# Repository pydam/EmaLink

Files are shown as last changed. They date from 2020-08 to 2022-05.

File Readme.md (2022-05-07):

# EmaLink

A device that bridges the communication between Loop software application and Omnipod and Medtronic insulin pumps. This is a fork from RileyLink, focusing on reducing size of the device, improving communication range and extending battery life. Also, you can charge EmaLink with any micro USB charger - much broader available vs. the mini port USB used by RileyLink.

### Turning on
Use a nail, a small plastic or a wood bit to move the power switch towards the USB port. When EmaLink is powered on, you should see a red and a green LED turning on for 1 second.

### Connecting EmaLink to Loop/FreeAPS/AndroidAPS
Please follow the instructions provided by each application for connecting to EmaLink, the procedure is the same as for RileyLink, just the name of the device will be EmaLink.Once EmaLink is connected to Loop/FreeAPS/AndroidAPS, a green led will start blinking every 3 seconds on EmaLink.

### Charging

Once the battery gets almost depleted, a red led will start blinking every 3 seconds.
To charge it, you can use any micro USB charger from a phone, tablet, headset or another device. You can even use a power bank to charge it if it has a micro USB cable. Charging is considered finished after the red led (the one close to the USB connector) is turned off. It may take up to 3 hours for Nano.
For QI versions, charging can be also done with any QI compatible charge. Place EmaLink with the coil (you can see a round, copper coil, through the case) down on the middle of the QI charger and check that a red led is lighting from the top of the EmaLink. Once charging is completed, you should remove EmaLink from the charger as the charger reduces communication range.
Charging can be done every few days until EmaLink is fully charged (the red led turned off) or for a few minutes every day, depending on your schedule. Overnight charging also works well with a Micro USB charge but avoid leaving QI versions on the QI charger overnight as this reduced communication range and may generate red loops.

### LED Lights 

There are 3 leds on the back of the device: a red one, close to the micro USB charging port, and a red + green cluster on the other side. First, turn the EmaLink on by flipping the switch located next to the micro USB port. After you switch-on EmaLink, the red + green cluster will light-up for 1 second. When you connect EmaLink to AAPS on Loop over bluetooth, the green led will start blinking every 3 seconds. The green led will stop blinking once battery is almost depleted. The red led will start blinking once battery is almost depleted, you should consider charging it in the next few hours.

### Case

I have designed a new case to be 3D printed with TPU material. TPU is a flexbile material that cannot be shattered, this makes EmaLink
drop proof. There are several case styles to chose from, pick the one that makes most sense for your needs.

### Hardware

See the [hardware](https://github.com/sks01/emalink/tree/master/hardware) directory for design files to build it. The hardware design is released under [Creative Commons Share-alike 3.0](http://creativecommons.org/licenses/by-sa/3.0/).  

### Firmware

The code in the [firmware](https://github.com/sks01/emalink/tree/master/firmware) directory runs on the hardware.  There are two main chips and thus two firmware images.
Check the "EmaLink 3_7 3_8 - firmware update guide.docx" if you would like to understand how you can update the firmware for EmaLink with PCB version 3.7, 3.8 or 3.9.

Check the "EmaLink 3_2 3_3 - firmware update guide.docx" if you would like to understand how you can update the firmware for EmaLink with PCB version 3.2 or 3.3. You can use breadboard wires also but you may need to keep them at an angle while flashing as the PCB holes are slightly bigger.

Check the "EmaLink%204_4%20-%20firmware%20update%20guide.pdf" if you would like to understand how you can update the firmware for EmaLink with PCB version 4.x. 

### License

The MIT License (MIT)

Copyright (c) 2015 Pete Schwamb

Permission is hereby granted, free of charge, to any person obtaining a copy
of this software and associated documentation files (the "Software"), to deal
in the Software without restriction, including without limitation the rights
to use, copy, modify, merge, publish, distribute, sublicense, and/or sell
copies of the Software, and to permit persons to whom the Software is
furnished to do so, subject to the following conditions:

The above copyright notice and this permission notice shall be included in all
copies or substantial portions of the Software.

THE SOFTWARE IS PROVIDED "AS IS", WITHOUT WARRANTY OF ANY KIND, EXPRESS OR
IMPLIED, INCLUDING BUT NOT LIMITED TO THE WARRANTIES OF MERCHANTABILITY,
FITNESS FOR A PARTICULAR PURPOSE AND NONINFRINGEMENT. IN NO EVENT SHALL THE
AUTHORS OR COPYRIGHT HOLDERS BE LIABLE FOR ANY CLAIM, DAMAGES OR OTHER
LIABILITY, WHETHER IN AN ACTION OF CONTRACT, TORT OR OTHERWISE, ARISING FROM,
OUT OF OR IN CONNECTION WITH THE SOFTWARE OR THE USE OR OTHER DEALINGS IN THE
SOFTWARE.

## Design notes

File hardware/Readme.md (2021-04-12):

# EmaLink Hardware

 *  Project_EL v4.3_2021-04-12_19-27-16.zip - EasyEDA project for version 4.3
 *  Schematic_EL v4.x.pdf - Schematic for versions 4.1-4.2
 *  Project_EL v4.1.zip - EasyEDA project for versions 4.1-4.2
 *  Gerber_EL v4.2 PCB.zip - Gerber files for version 4.2
 
### PCB Assembly

You will have to look at the schematic and the board design in Kicad to know where the parts go, and how they are oriented.

I use a hot-air rework station to solder the BLE113 module, the CC1110 chip, the USB connector, the 24Mhz crystal and the 3 power coils. The rest can be soldered with normal soldering station but require good soldering skills (especially the balun and the RF tuning network)

### License

The hardware design is released under [Creative Commons Share-alike 3.0](http://creativecommons.org/licenses/by-sa/3.0/).

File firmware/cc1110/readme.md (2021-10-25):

*  CC1110 firmware version 2.2.23 works only with BLE firmware 3.15 or above. Also, PCB version v4.0 or above is needed for these firmware versions.
*  CC1110 firmware version 2.2.22 works only with BLE firmware 3.15 or above. Also, PCB version v4.0 or above is needed for these firmware versions.
*  CC1110 firmware version 2.2.21 works only with BLE firmware 3.13. Also, PCB version v4.0 or above is needed for these firmware versions.
*  CC1110 firmware version 2.2.19 works only with BLE firmware 3.11

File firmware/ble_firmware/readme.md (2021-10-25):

*  BLE firmware version 3.17 and 3.18 version works only with CC1110 2.2.22 or 2.2.23 firmware. Also, PCB version v4.0 or above is needed for these firmware versions.
*  BLE firmware version 3.15 version works only with CC1110 2.2.22 firmware. Also, PCB version v4.0 or above is needed for these firmware versions.
*  BLE firmware version 3.13 version works only with CC1110 2.2.21 firmware. Also, PCB version v4.0 or above is needed for these firmware versions.
*  BLE firmware version 3.11 version works only with CC1110 2.2.19 firmware

The BLE firmware needs to be be unpacked and adjusted to offer best battery charge indication.

You will need to adjust 2 areas:
*  in file main.bgs, go through the sections that start with "#look-up table for..." and uncomment the one that seems to be for your battery. Contact the author if you don't manage to identify the right one based on the battery your EmaLink has. If you select another section versus the one selected by default, make sure to unselect the default section or you will get compilation errors.
*  in file main.bgs, search for "const voltage_adj =". You will need to replace the value 1000 with the value that is specific to your EmaLink. You can use the value noted in a corner of the EmaLink PCB, a value in between 970 and 1030. Or, execute the procedure below in case that value is not visible anymore.
*  measure current battery voltage with a multimeter. If the value is above 4.17v, you need to use EmaLink until the voltage drops a bit.
*  check the voltage as reported by EmaLink; to get the voltage from EmaLink, you need to connect to EmaLink with some BLE tool (I use BLE Scanner) and read the "BATTERY VOLTAGE" customer Characteristic, under the CUSTOM SERVICE offered by EmaLink. This is shown as a 16bit hex number. Convert it to decimal and divide by 100 to see the battery voltage (for ex., 0x0170 = 3.68v)
*  Once you have them both, calculate the factor as [measured battery voltage]/[reported battery voltage]1000. So if you have measured 4.16v while EmaLink reports 4.12v, you need a factor of 4.16/4.121000 = 1009. Edit main.bgs file to have "const voltage_adj = 1009" and flash again the firmware on BLE chip. 
*  Repeat the cycle, until the [measured battery voltage]=[reported battery voltage]

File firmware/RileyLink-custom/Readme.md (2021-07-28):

*  Use the RileyLink firmware update guides to update your RileyLink with the custom EmaLink firmware versions. 
*  The immediate change you will see, is that the green led will blink every 3 seconds when RileyLink is connected over Bluetooth. No other LED will turn on while using RileyLink.
*  There is no indication when you battery get almost depleted, plan to charge your RileyLink on a regular basis. You can see details about expected battery lifetime between changes in the Wiki pages.

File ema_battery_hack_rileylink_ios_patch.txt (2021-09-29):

diff --git a/RileyLinkBLEKit/RileyLinkDevice.swift b/RileyLinkBLEKit/RileyLinkDevice.swift
index 412404d..d01bb68 100644
--- a/RileyLinkBLEKit/RileyLinkDevice.swift
+++ b/RileyLinkBLEKit/RileyLinkDevice.swift
@@ -14,7 +14,10 @@ public enum RileyLinkHardwareType {
     case ema
     
     var monitorsBattery: Bool {
-        return self == .orange
+        if self == .riley {
+            return false
+        }
+        return true
     }
 }
 
@@ -91,6 +94,9 @@ public class RileyLinkDevice {
         
         if services.itemWithUUID(RileyLinkServiceUUID.secureDFU.cbUUID) != nil {
             return .orange
+        } else if services.itemWithUUID(RileyLinkServiceUUID.battery.cbUUID) != nil {
+            // this returns true for riley with ema firmware, need a different check
+            return .ema
         } else {
             return .riley
         }
diff --git a/RileyLinkKitUI/RileyLinkDeviceTableViewController.swift b/RileyLinkKitUI/RileyLinkDeviceTableViewController.swift
index 9fae599..c082249 100644
--- a/RileyLinkKitUI/RileyLinkDeviceTableViewController.swift
+++ b/RileyLinkKitUI/RileyLinkDeviceTableViewController.swift
@@ -137,7 +137,7 @@ public class RileyLinkDeviceTableViewController: UITableViewController {
         title = device.name
         
         switch device.hardwareType {
-        case .riley, .ema, .none:
+        case .riley, .none:
             deviceRows = [
                 .customName,
                 .version,
@@ -147,6 +147,21 @@ public class RileyLinkDeviceTableViewController: UITableViewController {
                 .frequency
             ]
             
+            sections = [
+                .device,
+                .rileyLinkCommands
+            ]
+        case .ema:
+            deviceRows = [
+                .customName,
+                .version,
+                .rssi,
+                .connection,
+                .uptime,
+                .frequency,
+                .battery
+            ]
+
             sections = [
                 .device,
                 .rileyLinkCommands
@@ -297,6 +312,9 @@ public class RileyLinkDeviceTableViewController: UITableViewController {
         switch device.hardwareType {
         case .riley:
             readDiagnosticLEDMode()
+        case .ema:
+            device.updateBatteryLevel()
+            readDiagnosticLEDMode()
         case .orange:
             device.updateBatteryLevel()
             device.orangeWritePwd()

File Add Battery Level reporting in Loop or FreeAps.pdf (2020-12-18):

## Background

EmaLink hardware and firmware was improved to report the estimate remaining battery capacity. The estimate is not perfect but should still be a decent indicator of remaining battery life. In order to see the remaining charge in Loop or FreeAps, you need to implement some changes to one of its components: rileylink_ios. There are 2 ways to do it, both require some software skills.

## Solution 1 (medium): use a different rileylink_ios in your build

Steps:
- start from Loop dev branch
- in the Cartfile, change from github "ps2/rileylink_ios" "dev" to github "Andrei0105/rileylink_ios" "battery-dev"
- delete cartfile.resolved or execute carthage update
- build loop; first build may fail but the second build always works

## Solution 2 (hard): create a patch for your rileylink_ios of choice

Apply this patch below to the rileylink_ios that you want to use. This may require some changes as rileylink_ios code might be already different

https://github.com/Andrei0105/rileylink_ios/commit/bdadeebf08977e7428b871b4ec696280328220d8

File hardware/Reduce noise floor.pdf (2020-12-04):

## Background

In some situations, the noise generated by the onboard switching power supply, is picked-up by the radio receiver and negatively impacts the communication between EmaLink and your pump. This was mostly observed with Omnipod versions of EmaLink.

All EmaLinks manufactured as of 22-Nov-2020 have be improved and tested to eliminate this potential issue.

## Solution 1 (hard): Filter battery ground

Tools and parts needed:
a. Soldering station
b. Soldering wire
c. A power inductor with inductance of 1.5-4.7uH and DC resistance of maximum 0.1ohm. See below some options that would work:
i. LBR2518T2R2M – available from DigiKey or Mouser
ii. DFE201612E-1R5M - available from DigiKey, Mouser or Farnell
Steps:

### 1. Put a solder blob on the left pad of the USB filtering capacitor

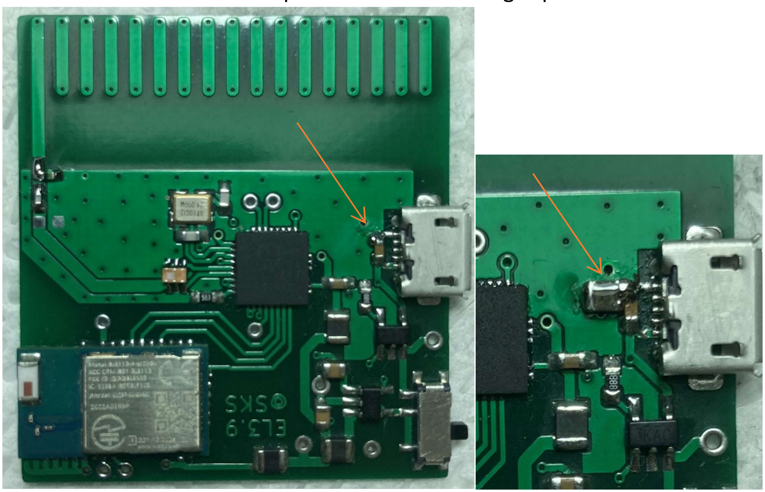
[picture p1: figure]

### 2. Solder one pad of the inductor to that solder blob

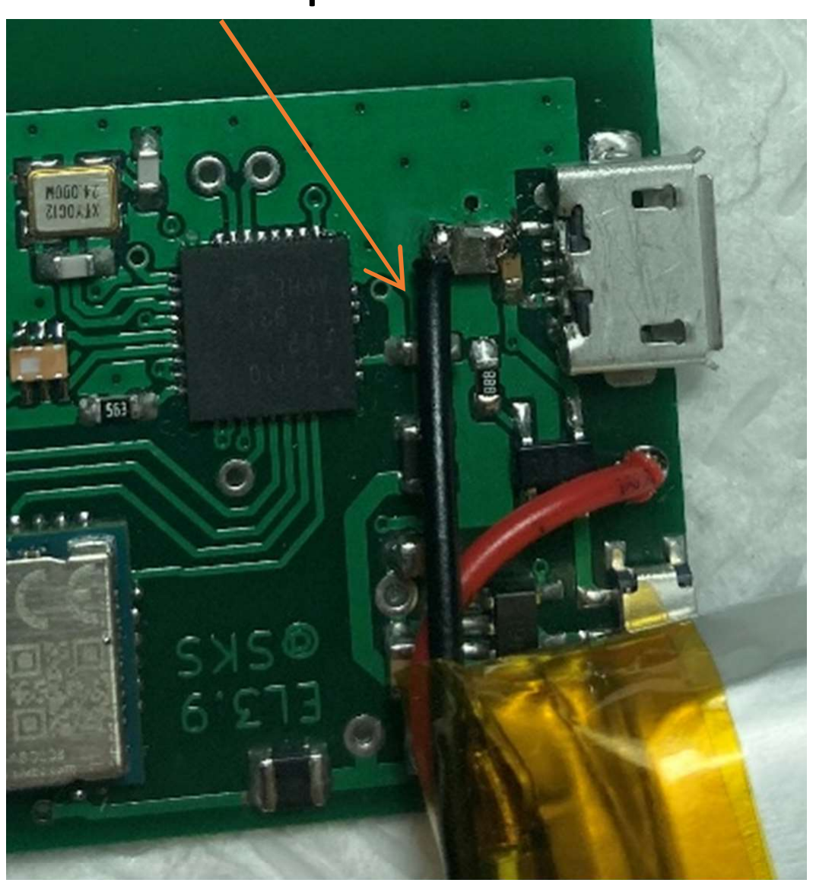
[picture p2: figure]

3. Unsolder the black battery wire from current position and solder it to the free pad of the inductor

## Solution 2 (easy): Increase gap between battery and CC1110

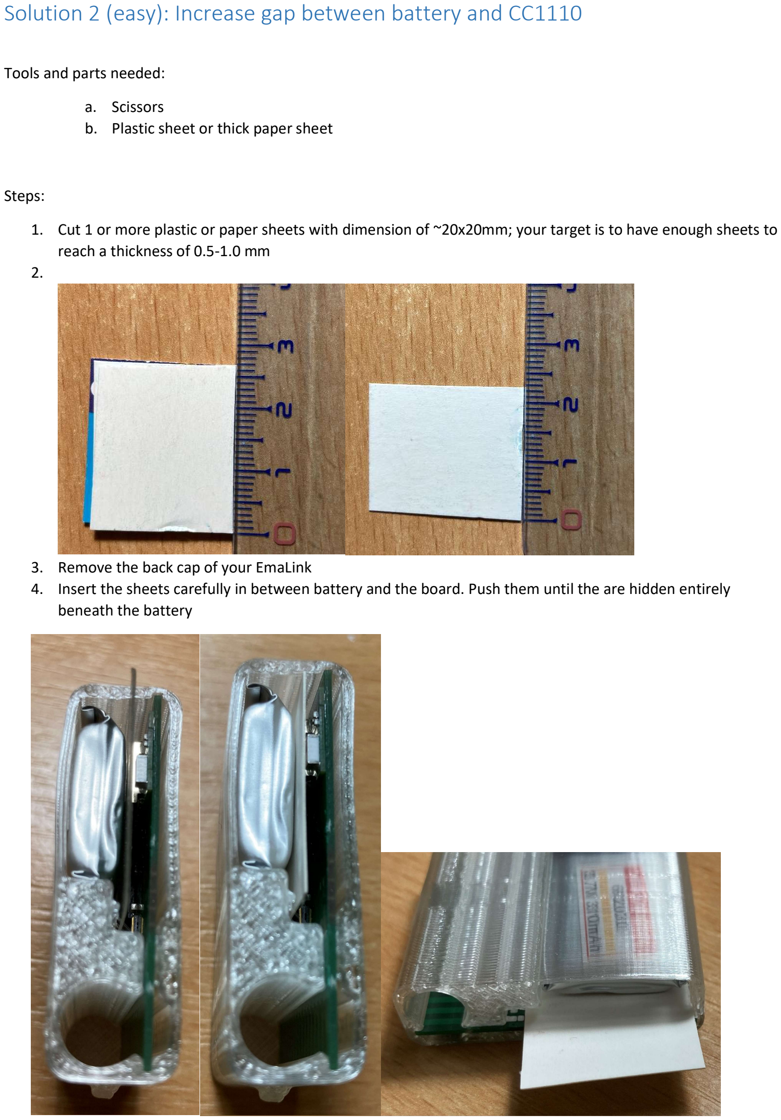
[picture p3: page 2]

Tools and parts needed:
a. Scissors
b. Plastic sheet or thick paper sheet

Steps:
1. Cut 1 or more plastic or paper sheets with dimension of ~20x20mm; your target is to have enough sheets to reach a thickness of 0.5-1.0 mm
2.

### 3. Remove the back cap of your EmaLink

4. Insert the sheets carefully in between battery and the board. Push them until the are hidden entirely beneath the battery

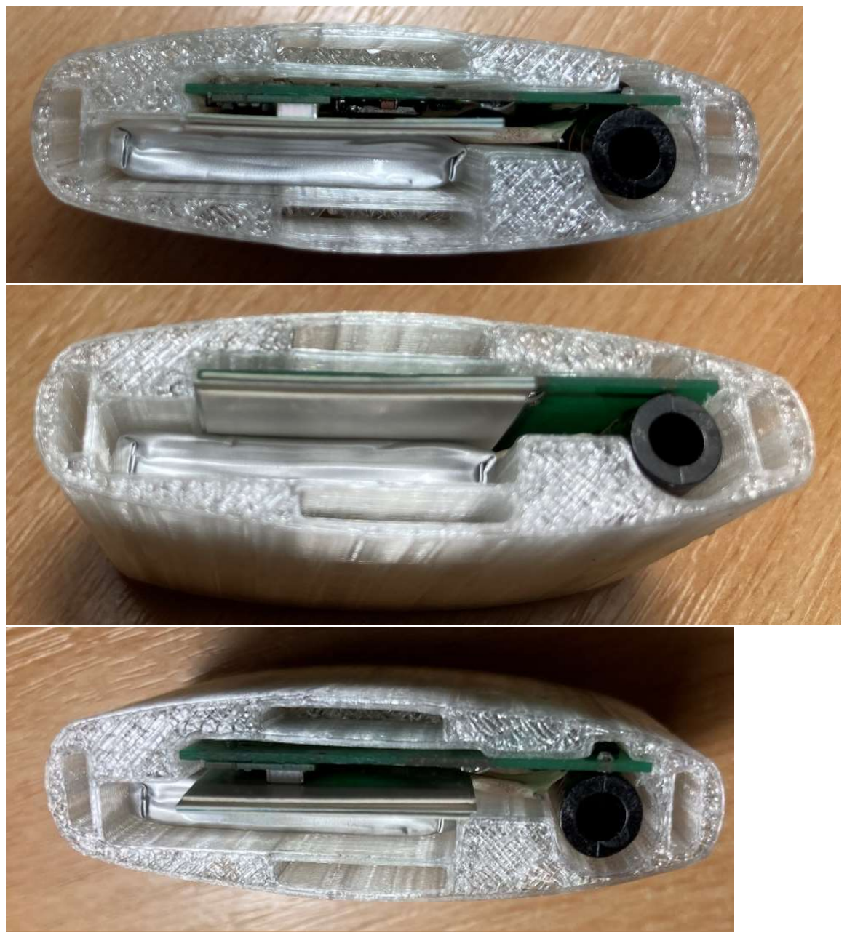
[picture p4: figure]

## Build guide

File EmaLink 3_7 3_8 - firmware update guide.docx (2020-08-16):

Prerequisites:

- CC Debugger (original (https://ro.farnell.com/texas-instruments/cc-debugger/debuggerprogrammer-for-rf-soc/dp/3009896?scope=partnumberlookahead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) – 50Euro or clone (https://www.ebay.com/itm/CC-Debugger-Bluetooth-ZigBee-Emulator-For-2530-2531-2540-2541-protocol-analysis/402021598624) 10-25Euro)
- Computer with Microsoft Windows 10 and at least one USB port available to connect
- SmartRF Studio from http://www.ti.com/tool/smartrftm-studio (Make sure to 'Extract All' if prompted at install/unzip time) ; you will need an account to download it
- http://www.ti.com/tool/FLASH-PROGRAMMER - install the old 1.12.8 version; you will need an account to download it

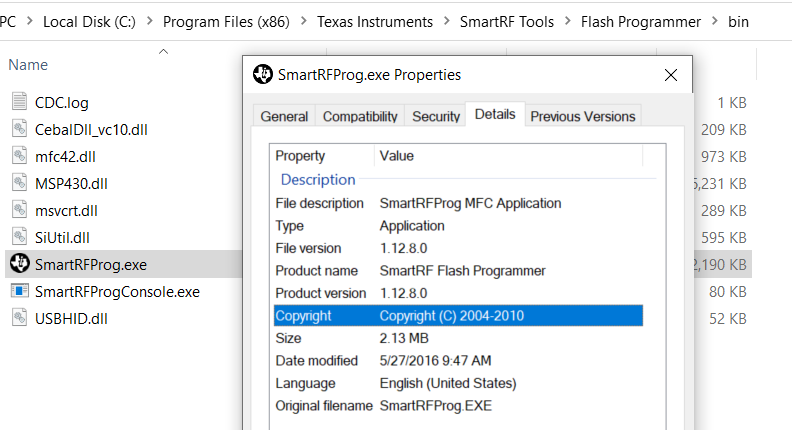
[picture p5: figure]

- "Bluetooth Smart Software and SDK v.1.8.0" (or above) from (https://www.silabs.com/documents/login/software/Bluegiga_ble-1.8.0-143.exe)
- 4 breadboard wires with a 0.6 tip

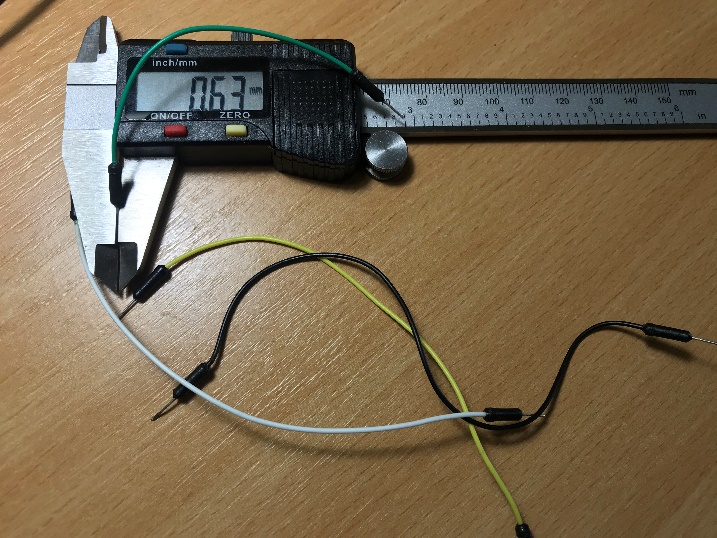
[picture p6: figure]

Hardware setup for flashing CC1110 (subg-rfspy):

- Plug the 4 wires to EmaLink as shown below

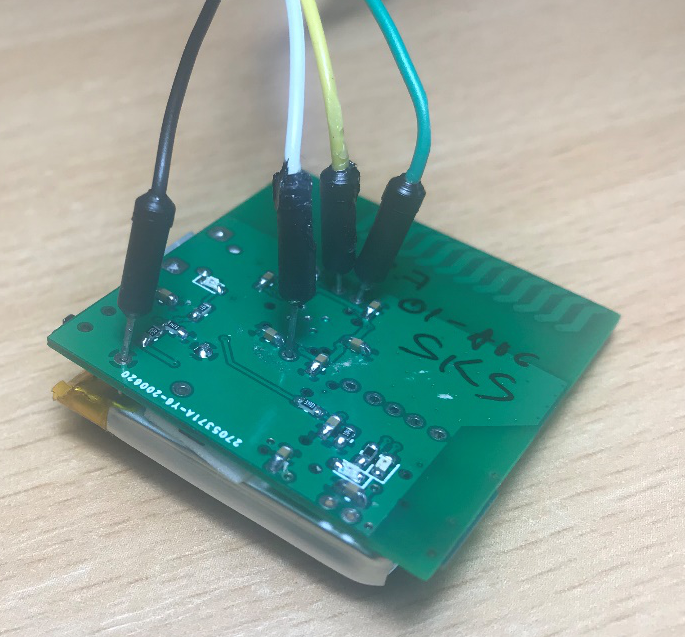
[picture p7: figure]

- Connect the wires to the CC cable like shown in the pictures below

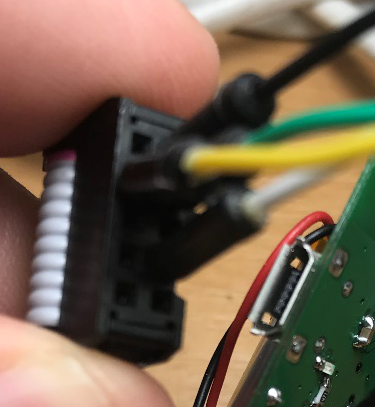
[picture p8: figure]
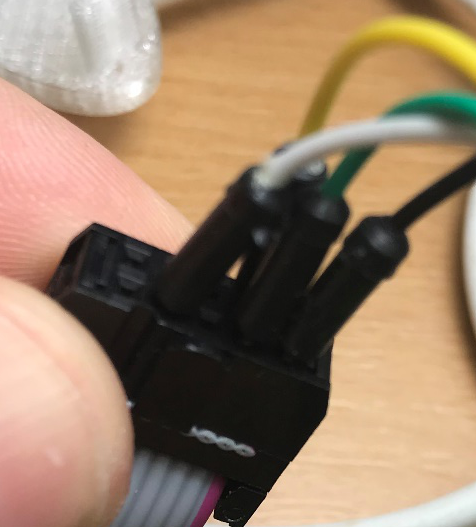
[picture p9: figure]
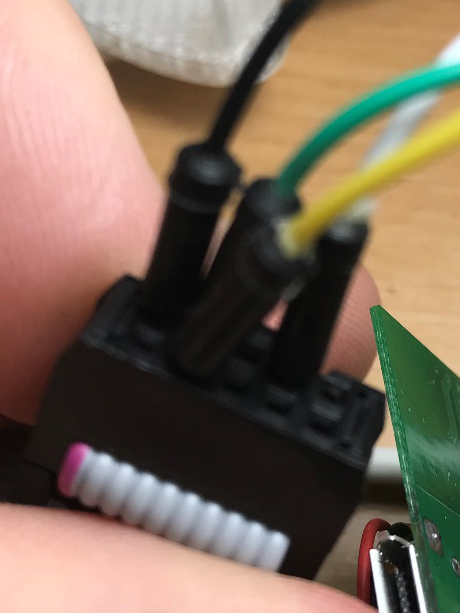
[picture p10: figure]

- Connect the other side of the cable to CC link and the USB cable to CC debugger. The final conection should look like below

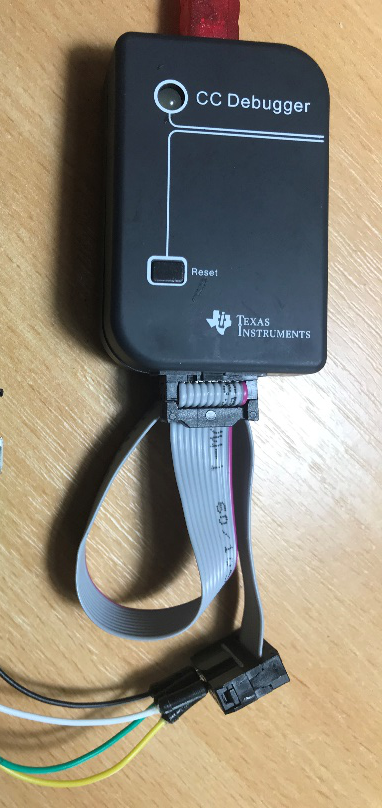
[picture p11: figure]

- Power ON EmaLink and push “Reset” button on CC debugger; the LED on CC Debugger should turn greed (a very dim green for a clone CC debugger)
- Start SmartRF Flash Programmer, select the .hex file in the “File image” and push “Perform Actions” button in it. After few seconds, the flashing an checking should be done
- Restart EmaLink to activate the new firmware

Hardware setup for flashing BLE113:

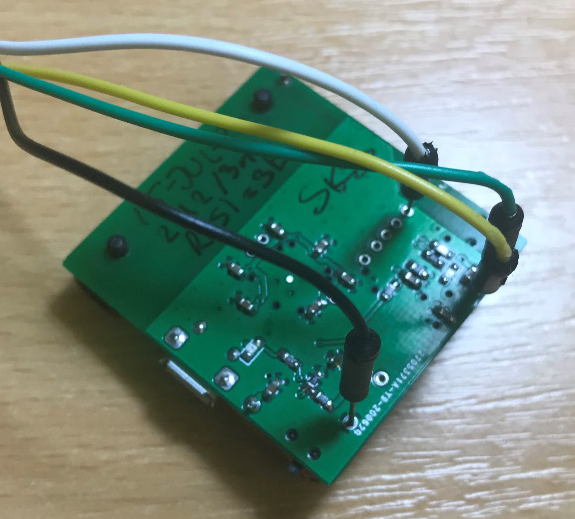
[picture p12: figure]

- Plug the 4 wires to EmaLink as shown below (the black wire has the same position as for CC1110)

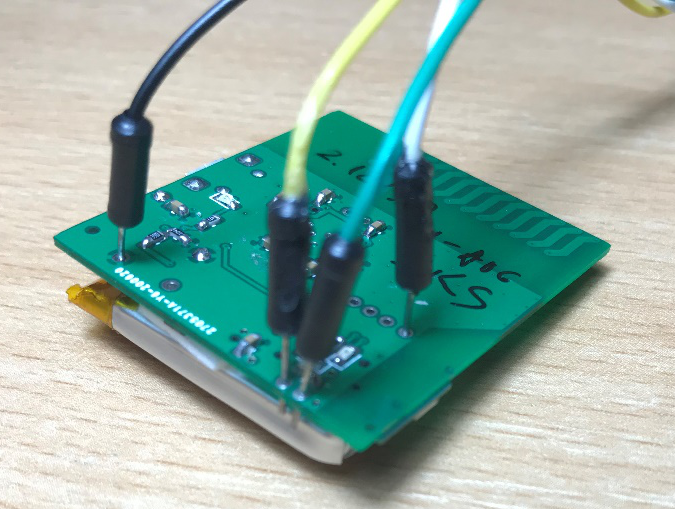
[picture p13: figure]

- The connections on CC Debugger side stay the same as for CC1110
- Power ON EmaLink and push “Reset” button on CC debugger; the LED on CC Debugger should turn greed (a very dim green for a clone CC debugger)
- Start Bluegiga BLE SW Update Tool, select the “project.bgproj” file from the current firmware version and push “Update” button in it. After few seconds, the flashing and checking should be done
- Restart EmaLink to activate the new firmware

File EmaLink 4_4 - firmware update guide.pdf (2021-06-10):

Prerequisites:

- CC Debugger (original (https://ro.farnell.com/texas-instruments/cc-debugger/debuggerprogrammer-for-rf-soc/dp/3009896?scope=partnumberlookahead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) – 50Euro or clone (https://www.ebay.com/itm/CC-Debugger-Bluetooth-ZigBee-Emulator-For-2530-2531-2540-2541-protocol-analysis/402021598624) 10-25Euro)
- Computer with Microsoft Windows 10 and at least one USB port available to connect
- SmartRF Studio from http://www.ti.com/tool/smartrftm-studio (Make sure to 'Extract All' if prompted at install/unzip time) ; you will need an account to download it
- http://www.ti.com/tool/FLASH-PROGRAMMER - install the old 1.12.8 version; you will need an account to download it

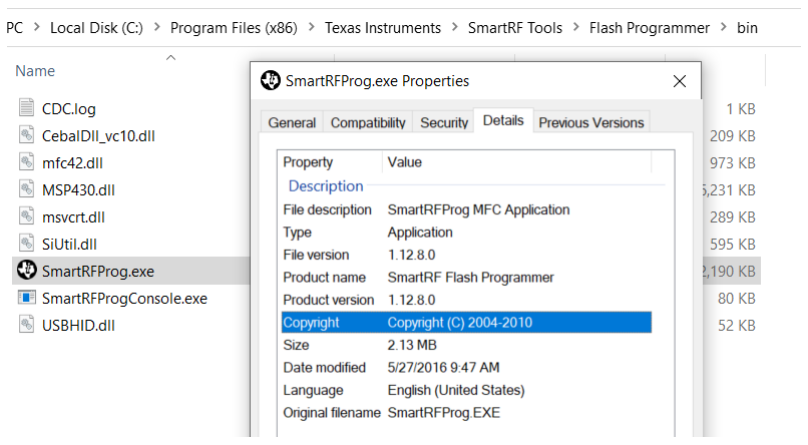
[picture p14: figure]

- "Bluetooth Smart Software and SDK v.1.8.0" (or above) from (https://www.silabs.com/documents/login/software/Bluegiga_ble-1.8.0-143.exe)
- 4 breadboard wires with a 0.6 tip

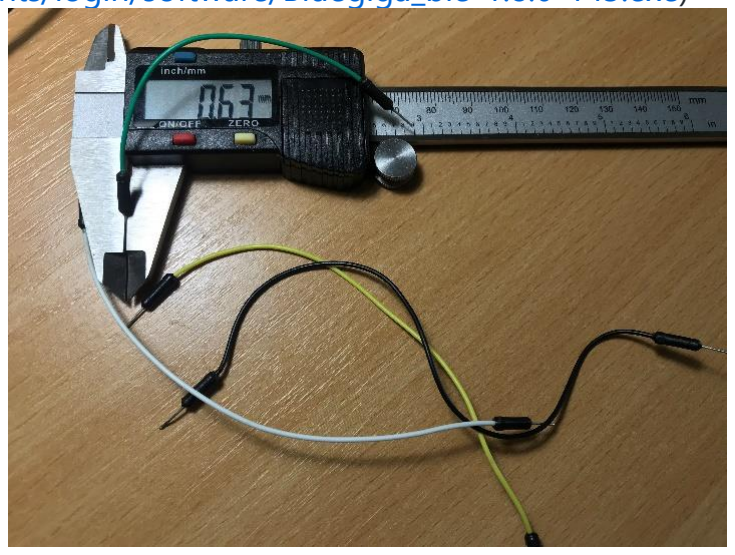
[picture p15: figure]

Hardware setup for flashing CC1110 (subg-rfspy):

- Plug the 4 wires to EmaLink as shown below (black and blue wire are the same, the color was change in between pictures)

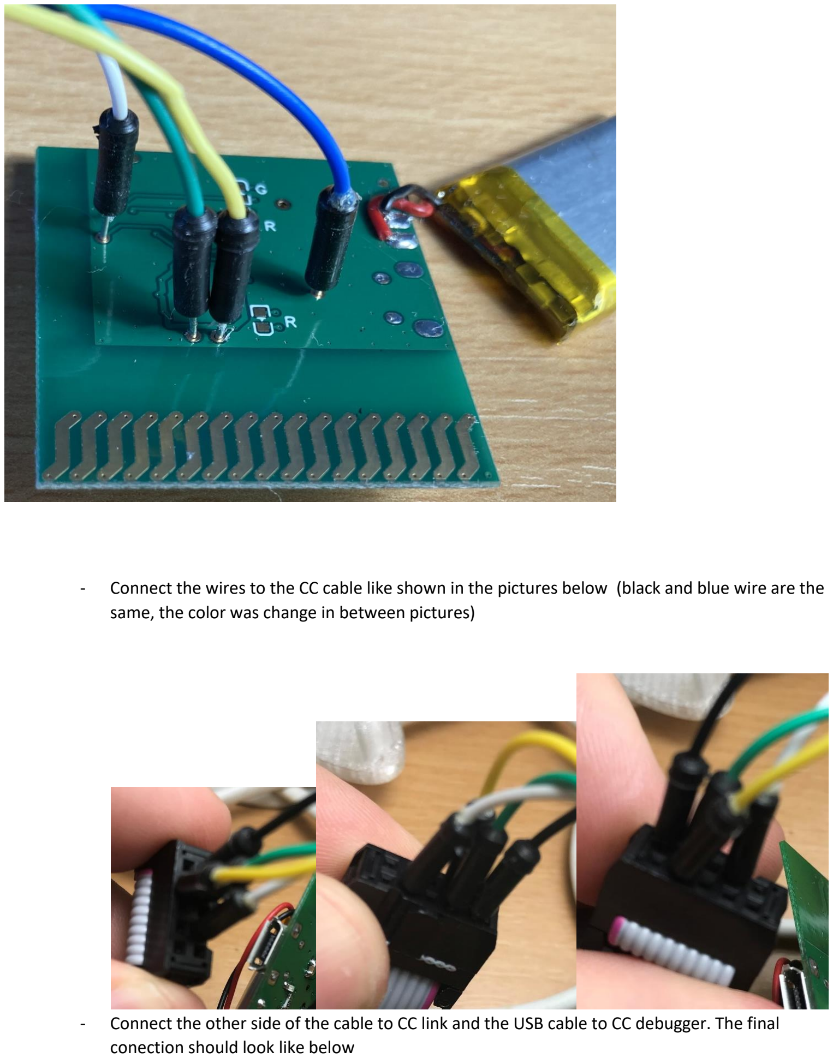
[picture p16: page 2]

- Connect the wires to the CC cable like shown in the pictures below (black and blue wire are the same, the color was change in between pictures)
- Connect the other side of the cable to CC link and the USB cable to CC debugger. The final conection should look like below

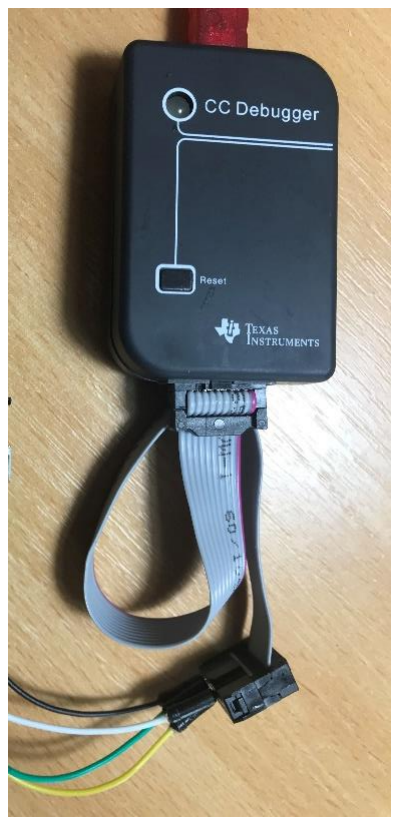
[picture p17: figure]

- Power ON EmaLink and push “Reset” button on CC debugger; the LED on CC Debugger should turn greed (a very dim green for a clone CC debugger)
- Start SmartRF Flash Programmer, select the .hex file in the “File image” and push “Perform Actions” button in it. After few seconds, the flashing an checking should be done
- Restart EmaLink to activate the new firmware

Hardware setup for flashing BLE113:

- Plug the 4 wires to EmaLink as shown below (the black/blue and white wires have the same position as for CC1110)

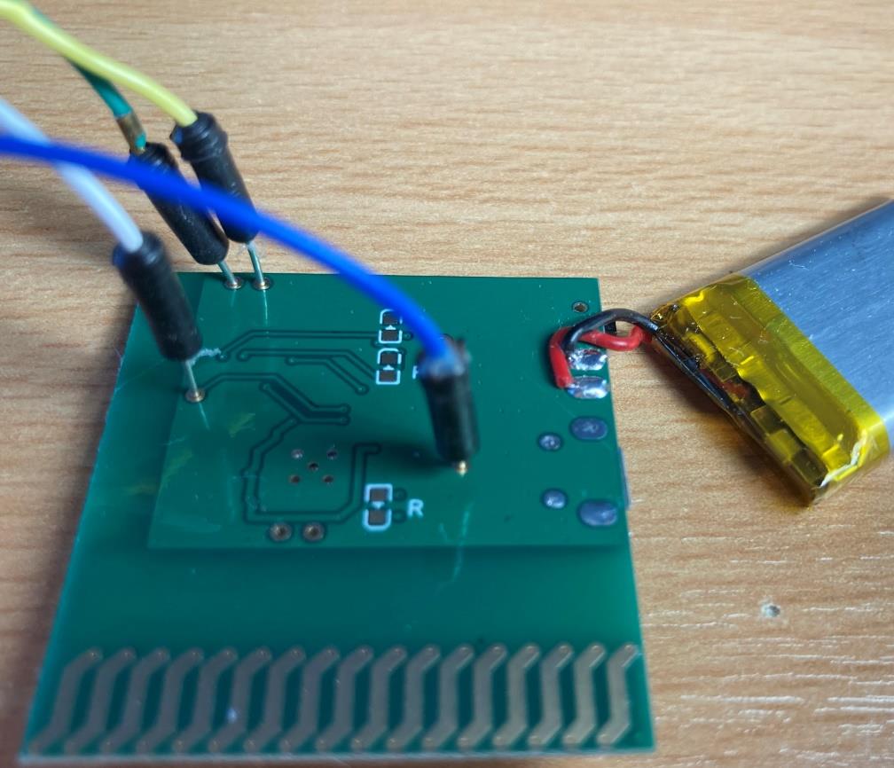
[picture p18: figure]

- The connections on CC Debugger side stay the same as for CC1110
- Power ON EmaLink and push “Reset” button on CC debugger; the LED on CC Debugger should turn greed (a very dim green for a clone CC debugger)
- Start Bluegiga BLE SW Update Tool, select the “project.bgproj” file from the current firmware version and push “Update” button in it. After few seconds, the flashing and checking should be done
- Restart EmaLink to activate the new firmware

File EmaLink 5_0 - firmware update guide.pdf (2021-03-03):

Prerequisites:

- CC Debugger (original (https://ro.farnell.com/texas-instruments/cc-debugger/debuggerprogrammer-for-rf-soc/dp/3009896?scope=partnumberlookahead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) – 50Euro or clone (https://www.ebay.com/itm/CC-Debugger-Bluetooth-ZigBee-Emulator-For-2530-2531-2540-2541-protocol-analysis/402021598624) 10-25Euro)
- Computer with Microsoft Windows 10 and at least one USB port available to connect
- SmartRF Studio from http://www.ti.com/tool/smartrftm-studio (Make sure to 'Extract All' if prompted at install/unzip time) ; you will need an account to download it
- http://www.ti.com/tool/FLASH-PROGRAMMER - install the old 1.12.8 version; you will need an account to download it


- "Bluetooth Smart Software and SDK v.1.8.0" (or above) from (https://www.silabs.com/documents/login/software/Bluegiga_ble-1.8.0-143.exe)
- 4 breadboard wires with a 0.6 tip

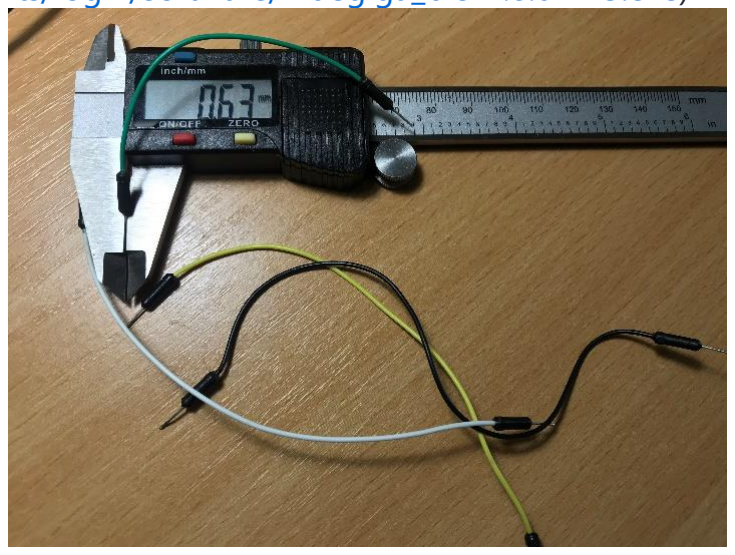
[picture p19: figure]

Hardware setup for flashing CC1110 (subg-rfspy):

- Plug the 4 wires to EmaLink as shown below (black and blue wire are the same, the color was change in between pictures)

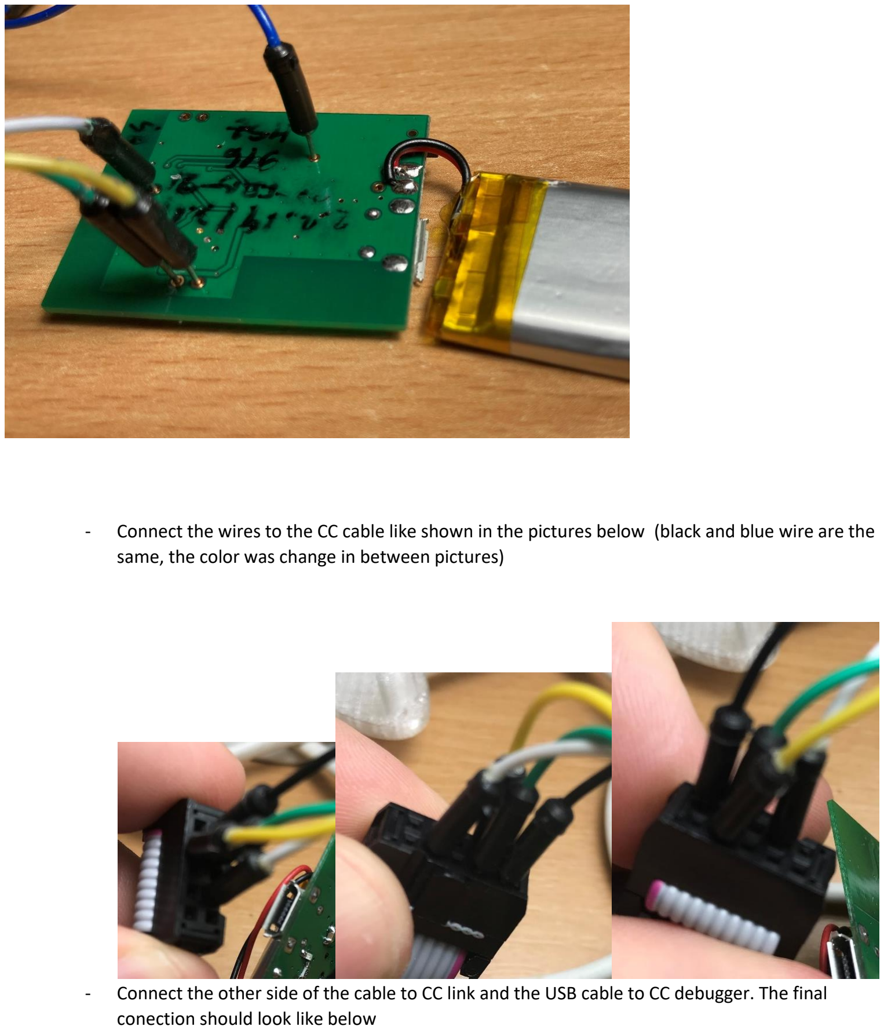
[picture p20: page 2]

- Connect the wires to the CC cable like shown in the pictures below (black and blue wire are the same, the color was change in between pictures)
- Connect the other side of the cable to CC link and the USB cable to CC debugger. The final conection should look like below

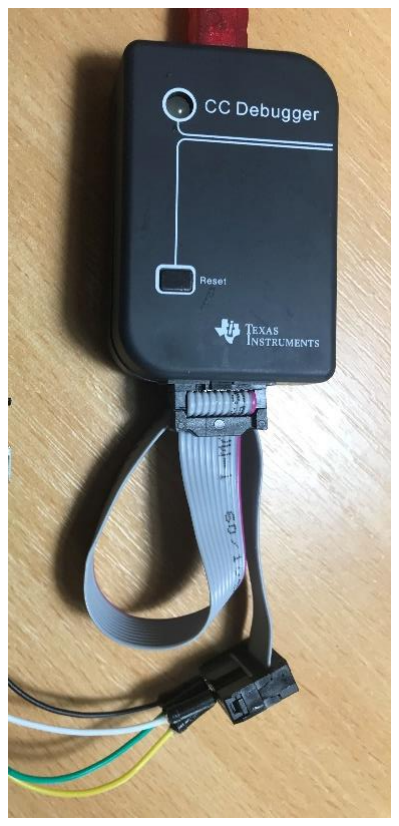
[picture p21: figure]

- Power ON EmaLink and push “Reset” button on CC debugger; the LED on CC Debugger should turn greed (a very dim green for a clone CC debugger)
- Start SmartRF Flash Programmer, select the .hex file in the “File image” and push “Perform Actions” button in it. After few seconds, the flashing an checking should be done
- Restart EmaLink to activate the new firmware

Hardware setup for flashing BLE113:

- Plug the 4 wires to EmaLink as shown below (the black/blue and white wires have the same position as for CC1110)

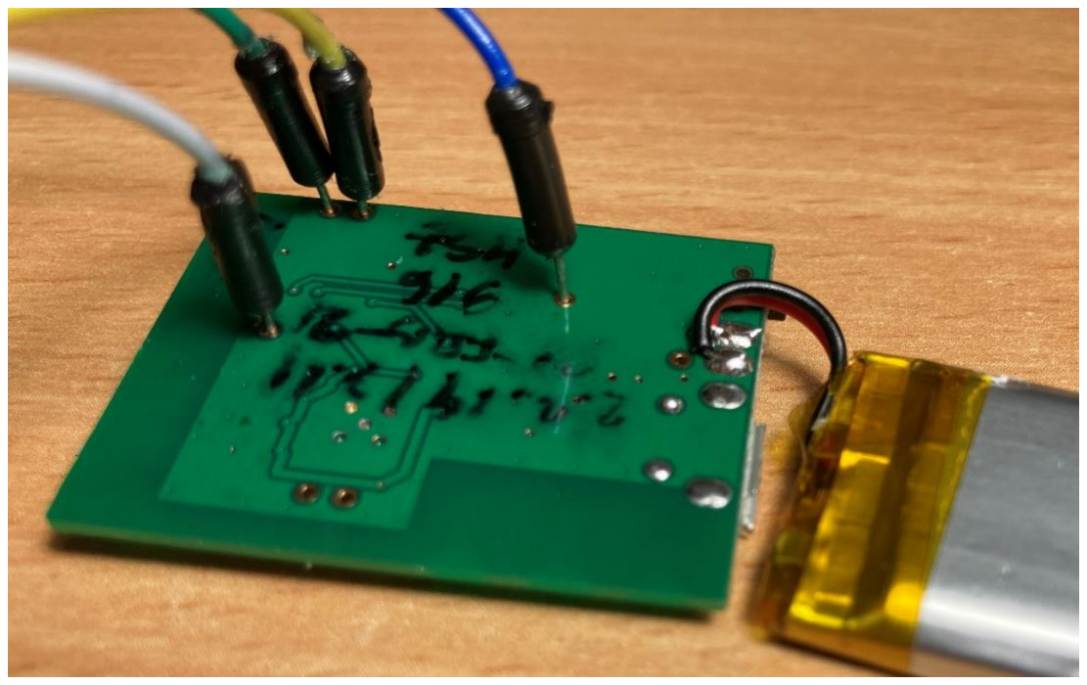
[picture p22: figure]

- The connections on CC Debugger side stay the same as for CC1110
- Power ON EmaLink and push “Reset” button on CC debugger; the LED on CC Debugger should turn greed (a very dim green for a clone CC debugger)
- Start Bluegiga BLE SW Update Tool, select the “project.bgproj” file from the current firmware version and push “Update” button in it. After few seconds, the flashing and checking should be done
- Restart EmaLink to activate the new firmware

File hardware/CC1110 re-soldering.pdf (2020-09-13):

## Re-solder CC1110 pins

This can be a fix in the following cases:
- You can connect to EmaLink over bluetooth but EmaLink does not communicate with Omnipod or Medtronic pumps (depending on EmaLink version)
- You have intermittent connectivity issues (red loops)
- You cannot re-flash CC1110 as CC debugger does not turn “green” after connecting and resetting it
ools needed:
a. Soldering station with a fine tip (I use a Weller station with a 0.6mm tip)
b. Soldering flux (I use AMTECH NC-559-V2-TF but any flux for RMA are good)
c. Soldering wire (I use a 0.35mm led + silver, Interflux IF14 Sn62Pb36Ag2)
d. Flux cleaner (I use isopropyl alcohol)

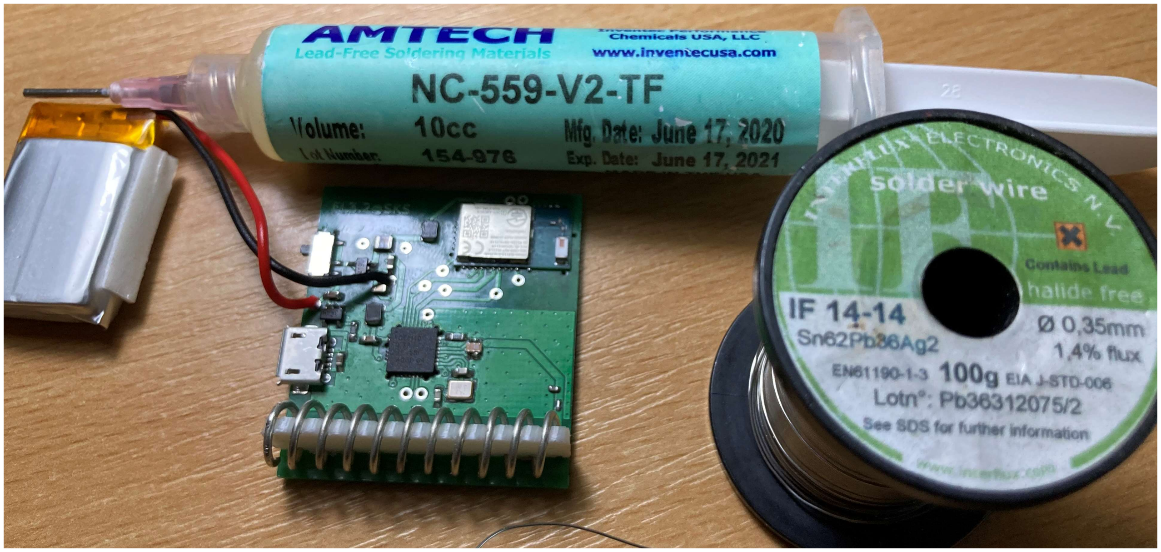
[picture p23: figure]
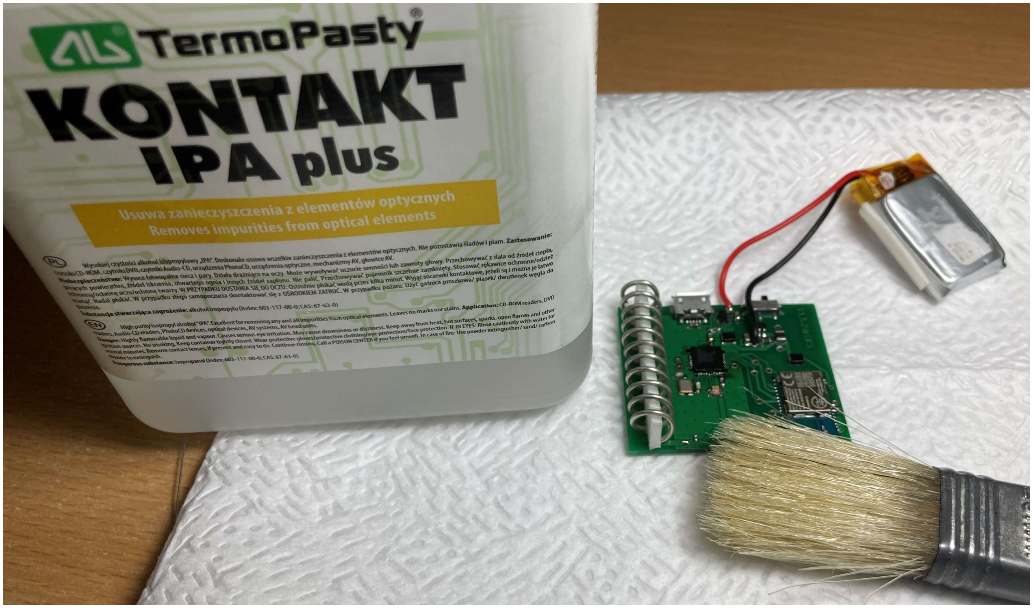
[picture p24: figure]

Steps:

### 1. Apply flux on the 4 sides of CC1110 chip

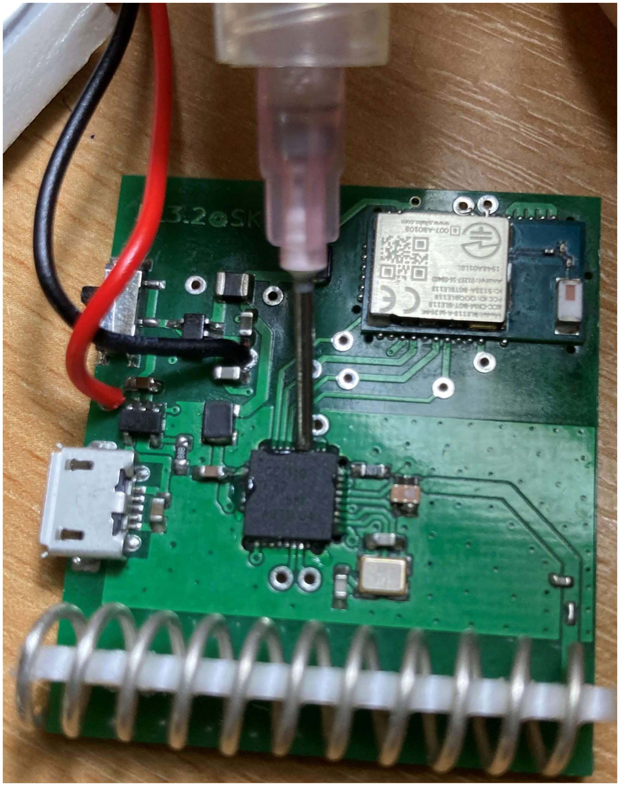
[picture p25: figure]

2. Re-solder all pins by slowly dragging the solder tip across all pins. Insist on pins where solder does not stick at first, they may be oxidized. At the end, all pins should look nice and shinny like the small picture below.

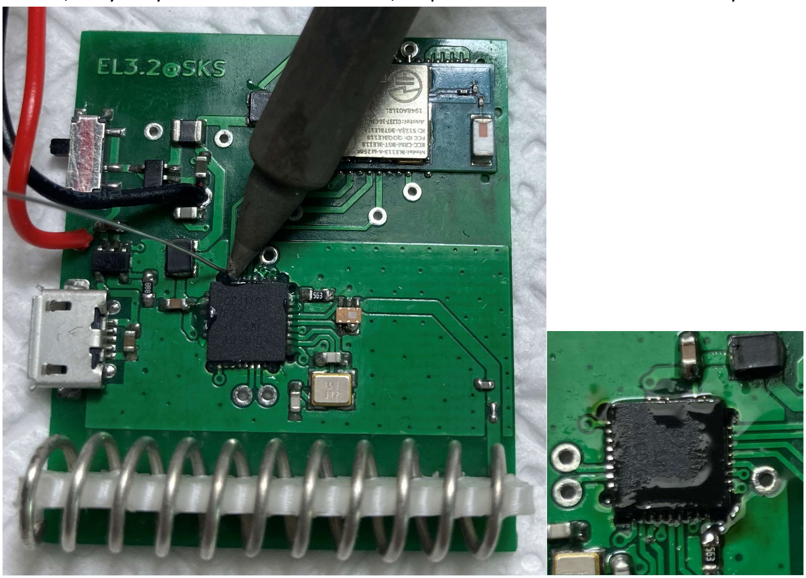
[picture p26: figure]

3. Inspect pins with a strong lens or microscope (no pictures available, I could not take pictures though the lens I use). Once I get an USB microscope, I’ll try again…

### 4. Clean remaining flux with Isopropyl alcohol and a brush

## Re-solder CC1110 ground plate

This can be a fix in the following cases:

- You can connect to EmaLink over bluetooth but EmaLink does not communicate with Omnipod or Medtronic pumps (depending on EmaLink version)
- You have intermittent connectivity issues (red loops)
- You cannot re-flash CC1110 as CC debugger does not turn “green” after connecting and resetting it
Tools needed:
e. 0.5mm drill bit + manual drill fixture (may work also with a sharp needle)
f. Soldering station with a fine tip (I use a Weller station with a 0.6mm tip)
g. Soldering flux (I use AMTECH NC-559-V2-TF but any flux for RMA are good)
h. Soldering wire (I use a 0.35mm led + silver, Interflux IF14 Sn62Pb36Ag2)
i. Flux cleaner (I use isopropyl alcohol)

Steps:

### 1. Use the drill bit to clean the solder mask from the 5 holes beneath CC1110 chip

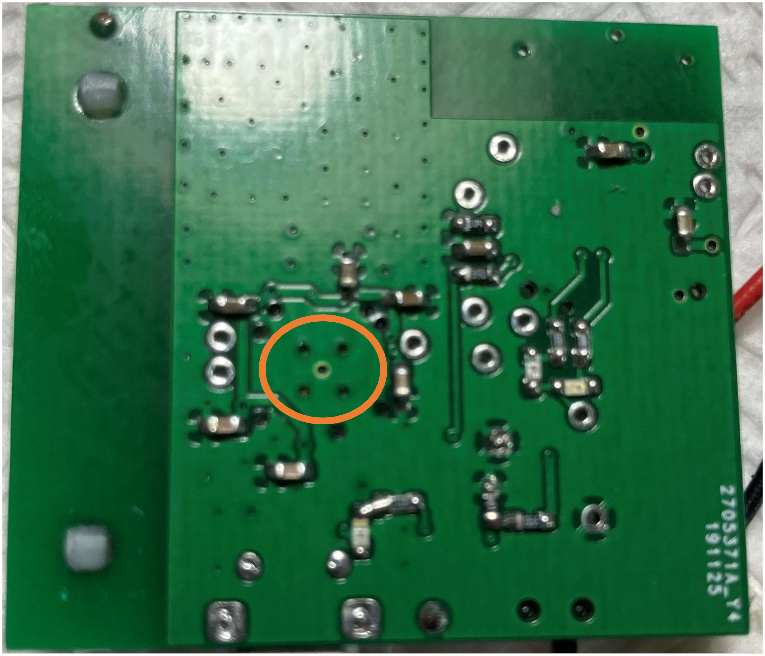
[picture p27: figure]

Use the drill to remove the solder mask, no need to push hard. Stop when you see the silver back of the CC1110 chip through each hole

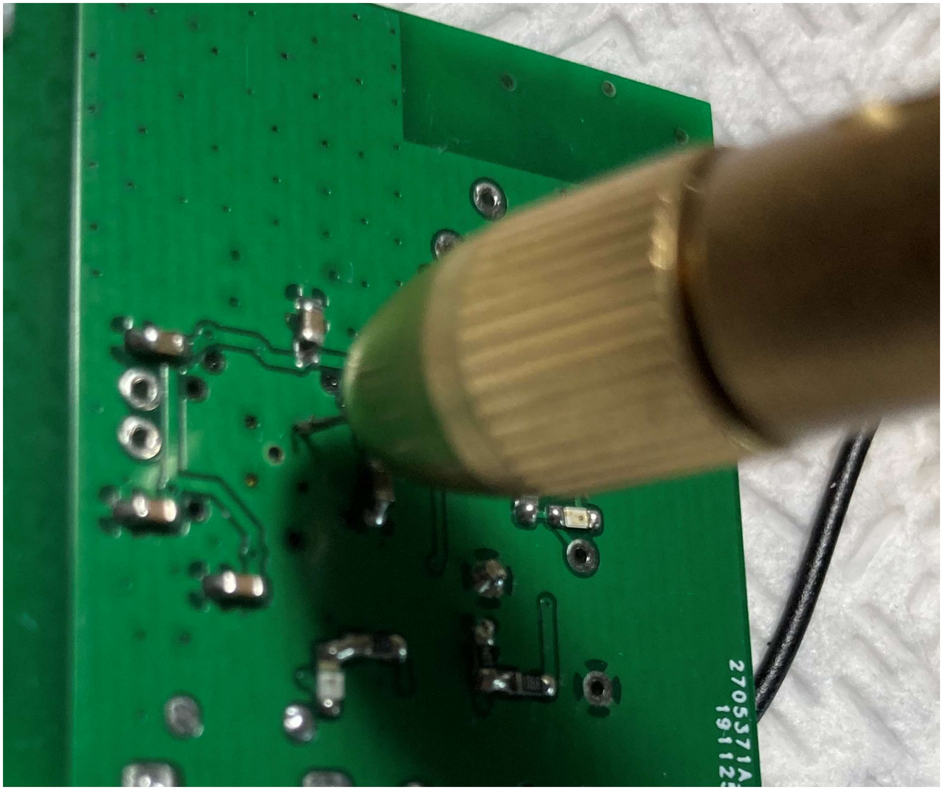
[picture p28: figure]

2. Apply flux and then put the solder tip (with solder wire on it) on the big hole in the middle. Heat-up until you see the flux bubling and you can melt solder in the 4 smaller holes. Insert the solder wires in each of the 4 small holes and keep it there until in melts inside.

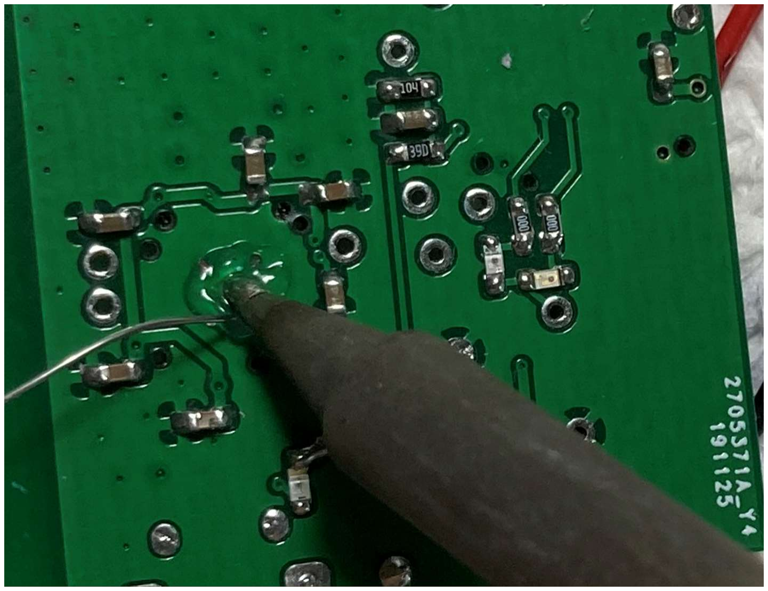
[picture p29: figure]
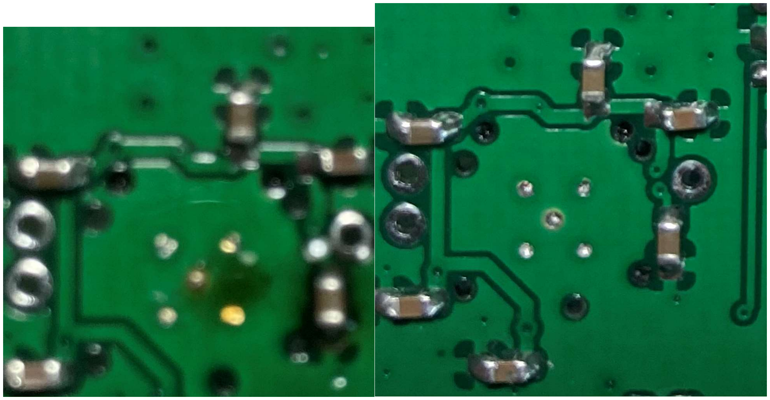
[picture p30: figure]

At the end, you want each hole (or at least as many as you can) full with solder.
3. Clean the back of the PCB with a tissue that has flux cleaner on it.

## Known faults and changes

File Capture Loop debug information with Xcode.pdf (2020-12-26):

## Background

Loop captures a very limited amount of information in the issue log, most times this information is not enough for debugging your issue. This document describes how you can capture more debug information, by using Xcode.

## How to capture debug information with Xcode

Steps:

### 1. Start your Mac, Hackintosh or Virtual Machine running MacOS

2. Connect your iPhone to the Mac; keep the phone connected and unlocked for the entire session

### 3. Start Xcode and open the project you last built to get Loop installed on your iPhone

a. Make sure that your phone is selected as the target device

### 4. Go to Product -> Perform Action -> Run Without Building

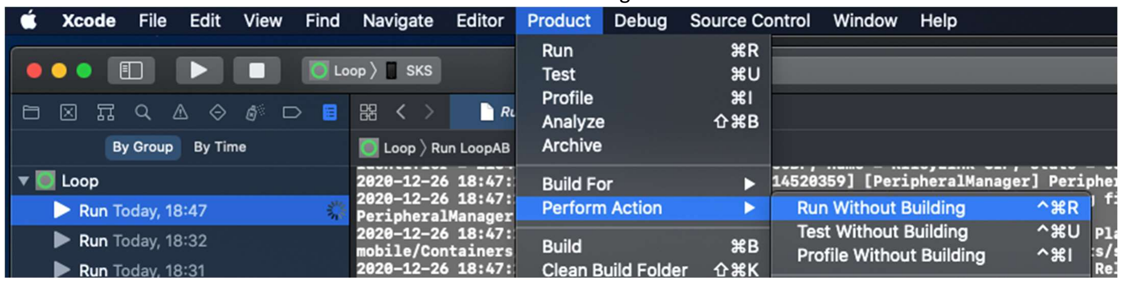
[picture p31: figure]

5. Switch the view to the Report Navigator (the blue icon just below “Loop” in the screenshot above)
6. Select the “Run Today, xx:xx” that has a progress indicator (the selected blue line in the left side of the screenshot above)
7. In Loop, do the steps needed to reproduce the issue you are facing (pair with a Medtronic pump, send a bolus, …). If needed, let Loop run for a longer while, just keep the phone connected to the Mac.
8. Once you reproduced the issue, select the text in the big text box, copy it and paste it to a new document in TextEdit. Save the document and send it via email.

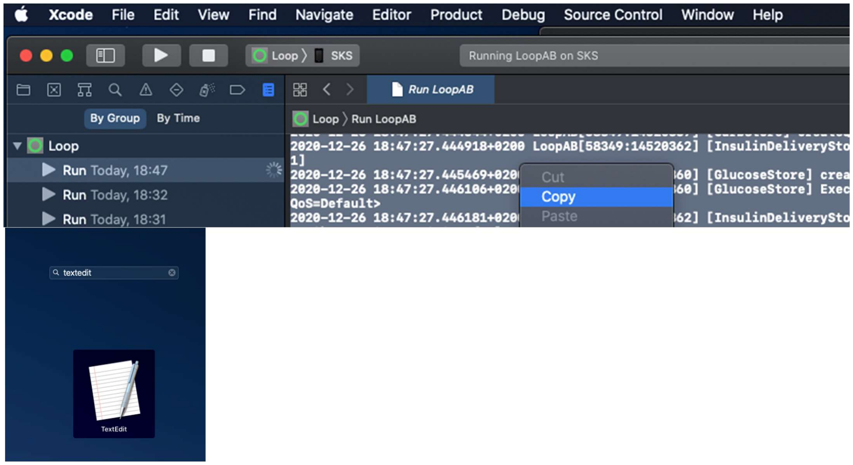
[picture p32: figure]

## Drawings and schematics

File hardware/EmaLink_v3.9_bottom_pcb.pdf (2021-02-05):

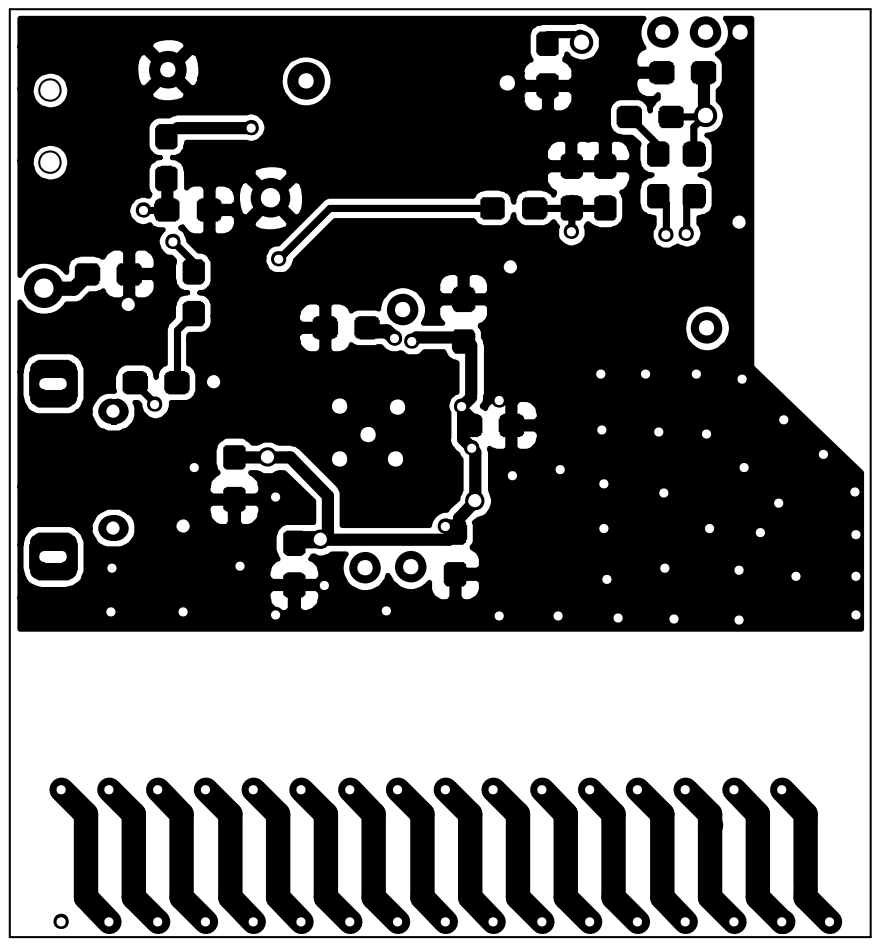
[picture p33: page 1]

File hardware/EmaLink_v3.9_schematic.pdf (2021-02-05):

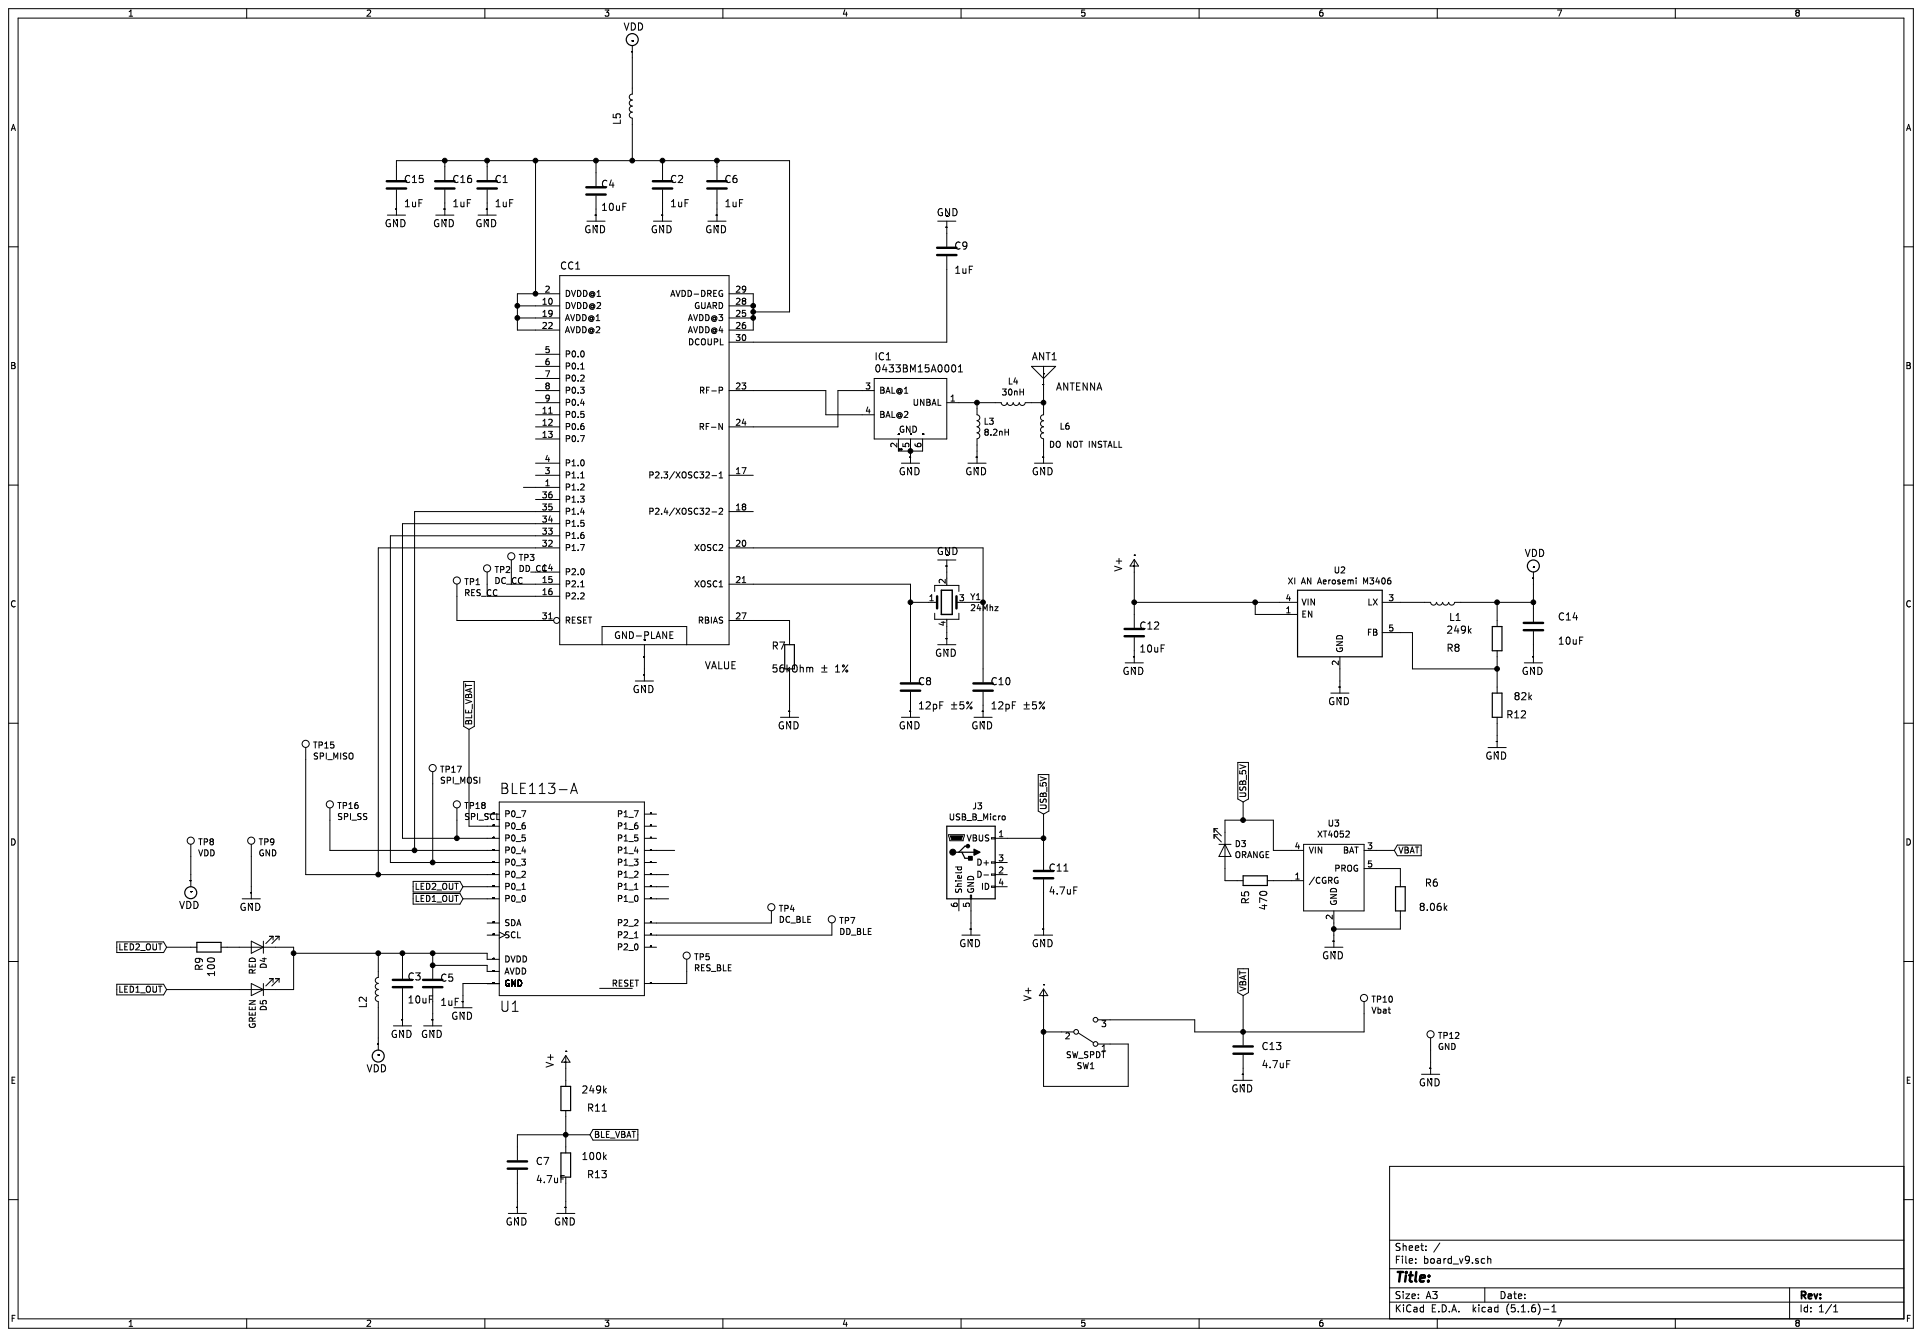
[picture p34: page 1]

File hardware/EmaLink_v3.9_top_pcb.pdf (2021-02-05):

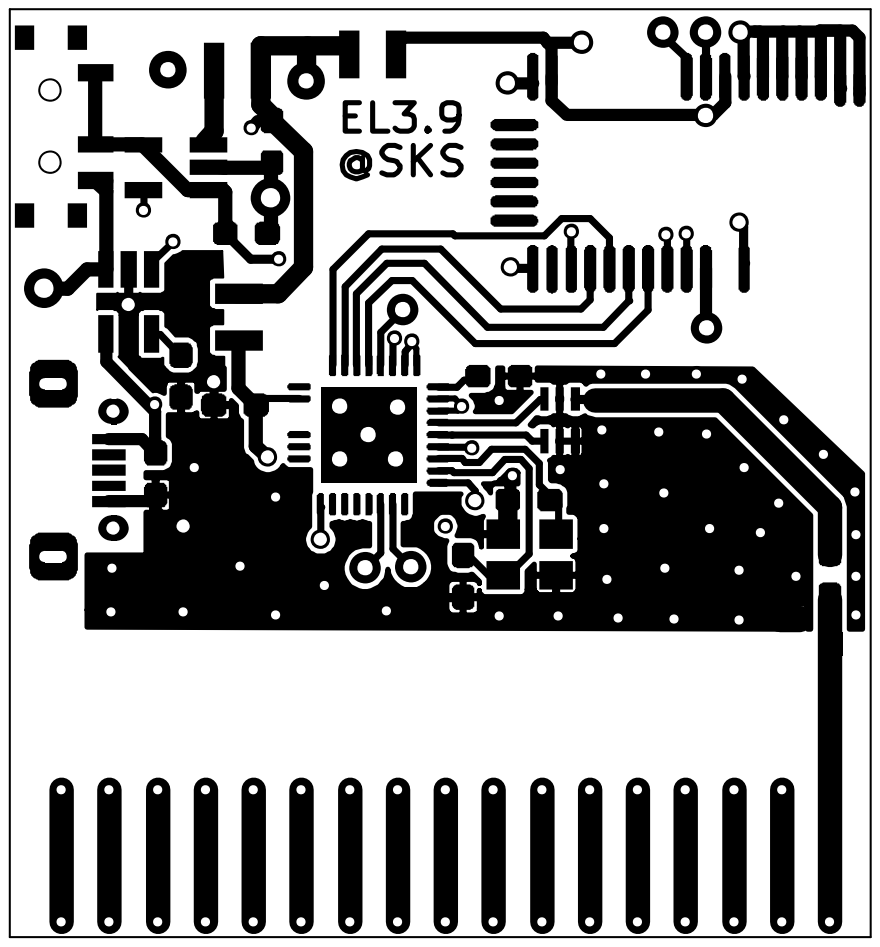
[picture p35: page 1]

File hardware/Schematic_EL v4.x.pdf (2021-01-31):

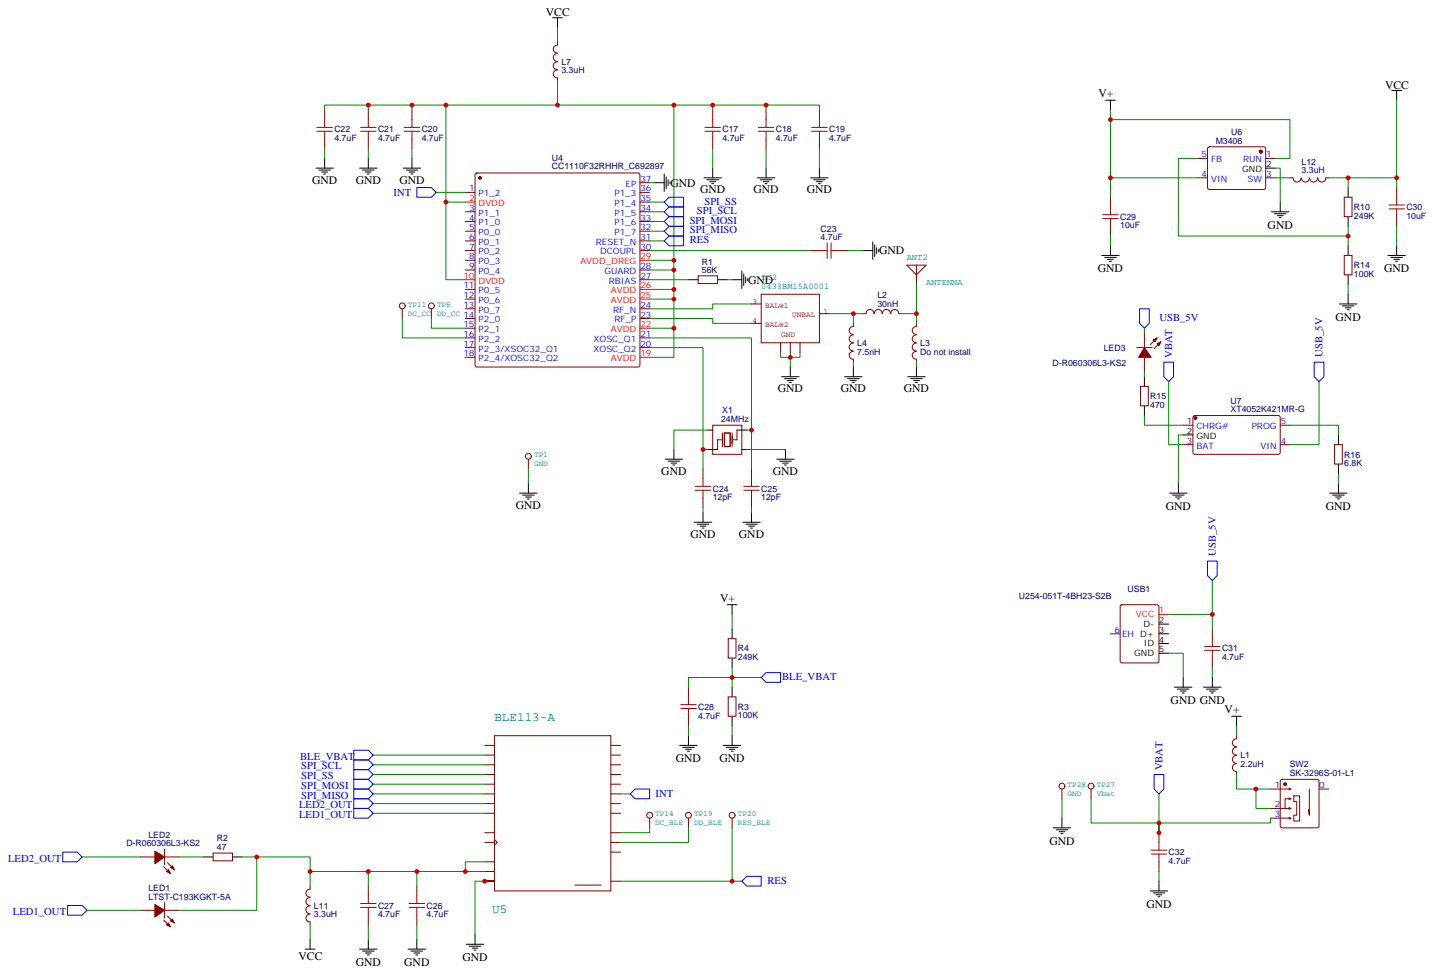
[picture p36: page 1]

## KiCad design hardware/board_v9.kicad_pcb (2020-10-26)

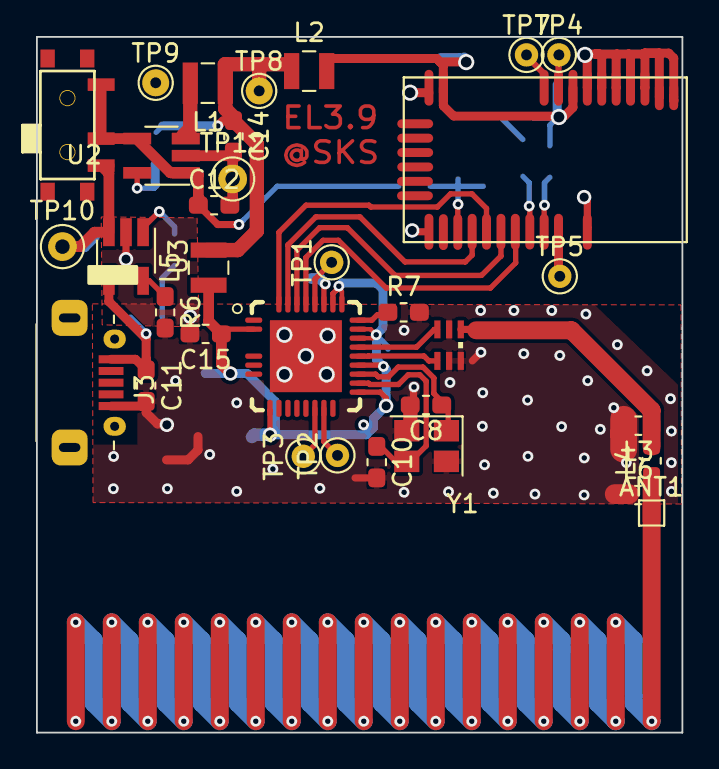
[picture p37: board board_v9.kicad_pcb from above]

Board: 2 copper layers, 35.9 x 38.6 mm, 52 parts (0 on the bottom side), 34 nets.

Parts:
ANT1: ANTENNA; TestPoint_Pad_1.0x1.0mm
C1, C2, C5, C6, C9, C15, C16: 1uF; C_0603_1608Metric_Pad1.05x0.95mm_HandSolder
C3, C4, C12, C14: 10uF; C_0603_1608Metric_Pad1.05x0.95mm_HandSolder
C7, C11, C13: 4.7uF; C_0603_1608Metric_Pad1.05x0.95mm_HandSolder
C8, C10: 12pF ±5%; C_0603_1608Metric_Pad1.05x0.95mm_HandSolder
CC1: CC1110; QLP-36_CC1110
D3: ORANGE; LED_0603_1608Metric_Pad1.05x0.95mm_HandSolder
D4: RED; LED_0603_1608Metric_Pad1.05x0.95mm_HandSolder
D5: GREEN; LED_0603_1608Metric_Pad1.05x0.95mm_HandSolder
IC1: 0433BM15A0001
J3: USB_B_Micro; U254-051T-4BH23-S2B
L1, L2, L5: 1.5u uH; L_Wuerth_MAPI-2512
L3: 6.8nH; L_0603_1608Metric
L4, L6: 12nH; L_0603_1608Metric
R5: 470; C_0603_1608Metric_Pad1.05x0.95mm_HandSolder
R6: 8.06k; C_0603_1608Metric_Pad1.05x0.95mm_HandSolder
R7: 56kOhm ± 1%; C_0603_1608Metric_Pad1.05x0.95mm_HandSolder
R8, R11: 249k; C_0603_1608Metric_Pad1.05x0.95mm_HandSolder
R9: 100; C_0603_1608Metric_Pad1.05x0.95mm_HandSolder
R12: 82k; C_0603_1608Metric_Pad1.05x0.95mm_HandSolder
R13: 100k; C_0603_1608Metric_Pad1.05x0.95mm_HandSolder
SW1: SW_SPDT; SLIDE_SWITCH_SMD
TP1: RES_CC; TestPoint_THTPad_D1.5mm_Drill0.7mm
TP2: DC_CC; TestPoint_THTPad_D1.5mm_Drill0.7mm
TP3: DD_CC; TestPoint_THTPad_D1.5mm_Drill0.7mm
TP4: DC_BLE; TestPoint_THTPad_D1.5mm_Drill0.6mm
TP5: RES_BLE; TestPoint_THTPad_D1.5mm_Drill0.6mm
TP7: DD_BLE; TestPoint_THTPad_D1.5mm_Drill0.6mm
TP8: VDD; TestPoint_THTPad_D1.5mm_Drill0.6mm
TP9: GND; TestPoint_THTPad_D1.5mm_Drill0.6mm
TP10: Vbat; TestPoint_THTPad_D2.0mm_Drill1.0mm
TP12: GND; TestPoint_THTPad_D2.0mm_Drill1.0mm
U1: BLE113-A
U2: XI AN Aerosemi M3406; SOT-23-5_HandSoldering
U3: XT4052; SOT-23-5_HandSoldering
Y1: 24Mhz; Crystal_SMD_3225-4Pin_3.2x2.5mm

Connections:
BLE_VBAT: C7.1, R11.1, R13.2, U1.P0_6
GND: C1.2, C2.2, C3.2, C4.2, C5.2, C6.2, C7.2, C8.2, C9.1, C10.2, C11.2, C12.2, C13.2, C14.2, C15.2, C16.2, CC1.37, IC1.2, IC1.5, IC1.6, J3.5, L3.2, L6.1, R6.2, R7.2, R12.1, R13.1, TP9.1, TP12.1, U1.GND, U1.GND@2, U1.GND@3, U1.GND@4, U1.GND@5, U1.GND@6, U1.GND@7, U1.GND@8, U1.GND@9, U1.GND@10, U2.2, U3.2, Y1.2, Y1.4
LED1_OUT: D5.2, U1.P0_0
LED2_OUT: R9.1, U1.P0_1
unnamed: ANT1.1, L4.1, L6.2
unnamed: C1.1, C2.1, C4.1, C6.1, C15.1, C16.1, CC1.2, CC1.10, CC1.19, CC1.22, CC1.25, CC1.26, CC1.28, CC1.29, L5.1
unnamed: C3.1, C5.1, D4.1, D5.1, L2.2, U1.AVDD, U1.DVDD
unnamed: C8.1, CC1.21, Y1.1
unnamed: C9.2, CC1.30
unnamed: C10.1, CC1.20, Y1.3
unnamed: CC1.15, TP3.1
unnamed: CC1.16, TP2.1
unnamed: CC1.23, IC1.4
unnamed: CC1.24, IC1.3
unnamed: CC1.27, R7.1
unnamed: CC1.31, TP1.1
unnamed: CC1.32, U1.P0_2
unnamed: CC1.33, U1.P0_3
unnamed: CC1.34, U1.P0_5
unnamed: CC1.35, U1.P0_4
unnamed: D3.2, R5.1
unnamed: D4.2, R9.2
unnamed: IC1.1, L3.1, L4.2
unnamed: L1.2, U2.3
unnamed: R5.2, U3.1
unnamed: R6.1, U3.5
unnamed: R8.1, R12.2, U2.5
unnamed: TP4.1, U1.P2_2
unnamed: TP5.1, U1.RESET
unnamed: TP7.1, U1.P2_1
USB_5V: C11.1, D3.1, J3.1, U3.4
V+: C12.1, R11.2, SW1.1, SW1.2, U2.1, U2.4
VBAT: C13.1, SW1.3, TP10.1, U3.3
VDD: C14.1, L1.1, L2.1, L5.2, R8.2, TP8.1

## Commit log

2020-02-03 PCB version 3.2
2020-02-03 Updated PCB
2020-02-16 Added BOM
    [bom_v4.xlsx]
2020-07-29 Updated for new PCB versions 3.7 and 3.8
2020-07-29 Added schematic and PCB version 3.7
    [board_v7.kicad_pcb, board_v7.sch]
2020-08-02 Update PCB pictures
2020-08-16 Added firmware update guide for 3.2 and 3.3 PCBs
2020-08-17 Added Medium case pictures
2020-08-17 Added Classic 3.2 case pictures
2020-09-13 Added instructions for solving soldering issues with CC1110 chip
2020-09-13 Added CC1110 re-soldering guide in PDF format
2020-09-18 Added 3.12 firmware for Omnipod users
    Use this firmware if you have communication issues (red loops) with Loop/FreeAPS and you currently have 2.12 firmware
2020-10-26 Added PCB version 3.9
    [board_v9.kicad_pcb, board_v9.sch]
2020-12-18 Add Battery Level reporting in Loop or FreeAps
2021-01-19 Added CC firmware 2.2.19
    Corrected bolus errors for Loop Medtronic users when using a Pump with MySentry feature
2021-01-19 EmaLink Power-on video
2021-02-05 Added files for PCB v3.9
    [board_v9.kicad_pcb, board_v9.sch]
2021-02-21 Added Nano PCB pictures
2021-03-03 Added firmware update guide for PCB v5.0 (Nano)
2021-04-23 Described the battery map calibration procedure
2021-09-29 battery level indicator patch for Loop v2.2.6
